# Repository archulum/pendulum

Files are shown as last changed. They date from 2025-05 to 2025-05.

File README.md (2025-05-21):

# The Electronic Pendulum by Arttu Lahti for Tampere University
This is the repository used to share important files and information on the Electronic pendulum BSc project. You can find the demo pendulum's 3D models, wiring diagram and parts list (with links) here. I also uploaded the Arduino scripts I used for my normal oscillation demos (both continuous and damped). The thesis itself is also here as a PDF file.

You're free to use and modify these files however you want, according to the MIT license (found in LICENSE.md).

For more information, check out the thesis.

Enjoy!

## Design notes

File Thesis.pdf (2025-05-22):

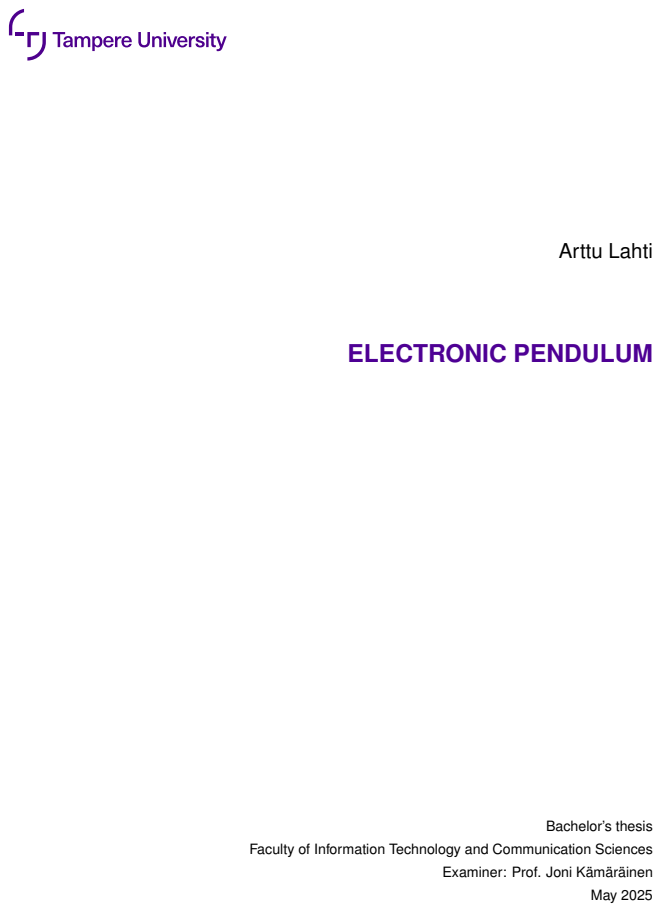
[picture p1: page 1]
Arttu Lahti; ELECTRONIC PENDULUM; Bachelor’s thesis; May 2025

Faculty of Information Technology and Communication Sciences

Examiner: Prof. Joni Kämäräinen

i

## ABSTRACT

Arttu Lahti: Electronic pendulum
Bachelor’s thesis
Tampere University
Bachelor’s Programme in Computing and Electrical Engineering May 2025

The pendulum is one of the simplest physical devices. Due to its simplicity, it is often represented on robotics, control and machine learning courses by simulations. However, there are upcoming courses at Tampere University, where the difference between simulations and the real world needs to highlighted, and a hands-on project is deemed beneficiary for the students. Given the predominant focus on simulations, there are very few, if any, simple electronic pendulums. This thesis explores existing research and projects already done on the subject, outlines the process of designing and building an electronic pendulum from scratch, and offers general instructions and an in-depth look into the thought process essential for building an electronic pendulum regardless of the available components.
Various article and thesis databases were consulted for the background information on past pendulum projects. One particular project stood out and was picked as the backbone of this project. The main electronic components of the pendulum are a DC motor, angular encoder, a motor driver and a single-board microcontroller. The components were picked carefully and it was made sure that they would work with each other. This process is detailed in the thesis, along with some things one must consider when doing the wiring work and designing the structure. Regarding the components and structure, some ideas and suggestions based on the difficulties experienced in building the demo pendulum are also provided along with the most critical warnings for the wiring. Some basic structural and functional testing was conducted and documented. The final demo product is a functional electronic pendulum that meets the testing criteria.

Keywords: robotics, pendulum, mechatronics, Arduino, electronics

The originality of this thesis has been checked using the Turnitin OriginalityCheck service.

ii

## TIIVISTELMÄ

Arttu Lahti: Elektroninen heiluri Kandidaatintyö
Tampereen yliopisto
Tieto- ja sähkötekniikan kandidaattiohjelma Toukokuu 2025

Heiluri on yksi yksinkertaisimmista fysikaalisista laitteista. Yksinkertaisuutensa vuoksi se saatetaan sivuuttaa robotiikan, säädön ja koneoppimisen kursseilla simulaatioiden tarjotessa lähes yhtä hyvän demonstraation. Tampereen yliopistolla on kuitenkin suunnitteilla kursseja, joissa oikean maailman ja simulaation ero on tarkoitus tuoda esille, ja mukaansatempaava fyysinen projekti olisi hyödyllinen opiskelijoille. Keskittyminen simulaatioihin on niin suurta, varsinkin tällä tasolla, että yksinkertaisia elektronisia heilureita on saatavilla erittäin heikosti, jos ollenkaan. Tässä työssä tutkitaan aiempia projekteja ja tutkimuksia, jotta saadaan käsitys saatavilla olevista heilureista ja työ käsittelee heilurin alusta asti suunnittelemisen ja rakentamisen vaiheet. Se myös tarjoaa yleisiä ohjeita ja syvemmän katsauksen siihen ajatusprosessiin, joka pitäisi olla perustana tällaista projektia toteuttavalla. Tarkoitus on, että tämän työn avulla henkilö pystyy suunnittelemaan ja rakentamaan elektronisen heilurin mistä vain saatavilla olevista osista.
Aluksi tutkittiin eri artikkeli- ja opinnäytetyötietokantoja taustatiedon keräämiseen aiemmista heiluriprojekteista. Yksi projekti valittiin tämän projektin perustaksi. Elektronisen heilurin tärkeimmät komponentit ovat tasavirtamoottori, kulmaenkooderi, moottoriohjain ja yhden levyn mikrokontrolleri. Komponentit valittiin huolella ja varmistettiin, että ne ovat toistensa kanssa yhteensopivia. Tämä prosessi on selitetty työssä johdotuksen ja rakenteen ohella. Työ tarjoaa myös yleisiä ohjeita ja ehdotuksia komponentteihin ja rakenteeseen liittyen perustuen demoheiluria rakennuksessa törmättyihin ongelmiin. Siinä on myös tämän kaltaiseen johdotukseen liittyviä varoituksia ja asioita, mitä ei kannata tehdä. Demoheilurille asetettiin ja tehtiin muutama perustesti liittyen rakenteeseen ja toimintaan. Valmis demoheiluri on toimiva elektroninen heiluri, joka täyttää testikriteerit.

Avainsanat: robotiikka, heiluri, mekatroniikka, Arduino, elektroniikka

Tämän julkaisun alkuperäisyys on tarkastettu Turnitin OriginalityCheck -ohjelmalla.

iii

## PREFACE

This was my first ever proper project involving electronics. When I saw the topics offered

to us, I decided to jump straight to the deep end, and here we are. I would like to extend my gratitude to Professor Joni Kämäräinen, my supervisor, for his support during every

part of the project and always being ready to listen and easy to communicate with. I would

also like to thank my friends and family for their support during the making of this project

and thesis.

Tampere, 22nd May 2025

Arttu Lahti

iv

The AI tools utilized in my thesis and their purposes are described below:

GPT-4o by OpenAI: GPT-4o was used to provide a massive help when figuring out the

electronic components and wiring of the pendulum to make sure everything is compatible

and safe. It was also a valuable and quick general assistant on different questions related

to the thesis.

ScopusAI by Elsevier: ScopusAI was used to find useful sources from Elsevier’s database

and to generate search words to use in Andor’s search function.

Apple Intelligence by Apple Inc.: Apple Intelligence provided fixes to the grammar and

structure of the entire text to ensure it is easy to understand and follows academic style.

I am aware that I am totally responsible for the entire content of the thesis, including

the parts generated by AI, and accept the responsibility for any violations of the ethical

standards of publications.

v

## CONTENTS

vi

## LIST OF SYMBOLS AND ABBREVIATIONS

b | viscous damping coefficient
cf | Coulomb friction coefficient
DC | Direct Current
E | total mechanical energy
g | gravity
I | moment of inertia
I/O | Input/Output
IDE | Integrated Development Environment
K | kinetic energy
L | pendulum arm length
m | pendulum mass
PC | Peak Current

PLA Polylactic Acid

RV | Rated Voltage
θ | angular position

θ

̇ angular velocity

θ

¨ | angular acceleration
TAU | Tampere University
τ | external torque from the motor
U | potential energy

## 1. INTRODUCTION

Pendulums are widely used in systems requiring control, mostly as benchmarking tools.

The most well-known example is the inverted pendulum, which is used in various exam-

ples, particularly in robotics and human locomotion analysis (Myers et al. 2020).

Most of the simple beginner-level control theory is taught with simulations. This may lead

students into thinking that physical real-world systems are as predictable as simulated environments, therefore, especially in robotics, learning with physical systems cannot

be substituted (Jara et al. 2011). A basic electronic pendulum provides students with

a connection to the real world that doubles as a physical, engaging, and dynamic system that can be used to experiment with control algorithms, reinforcement learning, and

signal processing. Due to the focus on simulations in entry-level studies, where simple

pendulums would be beneficial, simple electronic pendulums have been less explored

and documented. There were no readily available simple pendulums online that met the

criteria:

- reasonable tabletop size
- powered by a normal DC (Direct Current) motor
- able to follow programmed instructions to mimic realistic pendulum oscillation.

There are upcoming applications planned at TAU (Tampere University) for an electronic

pendulum on courses in robotics, signal processing, and machine learning. The objective of this thesis is not to provide a detailed tutorial on building an electronic pendulum, but

rather to offer insights into the thought process and the overall build and design process,

as well as the author’s considerations and reflections. Figure 1.1 depicts the 3D model of

the demo pendulum, whose design and building process was used to write this thesis.

The resources, such as models and scripts, used in building and testing the demo pendulum freely available at https://github.com/archulum/pendulum.

Chapter 2 provides an overview of control theory simulations, the fundamental principles

of a pendulum and various different designs for creating an electronic pendulum, and why

they do not fit the aim of this project. The aim of chapter 2 is not to go far into detail

on how a pendulum works, but highlight the phenomena that make a natural pendulum oscillate, aiming to provide further insight on how the motor could be controlled. Chapter

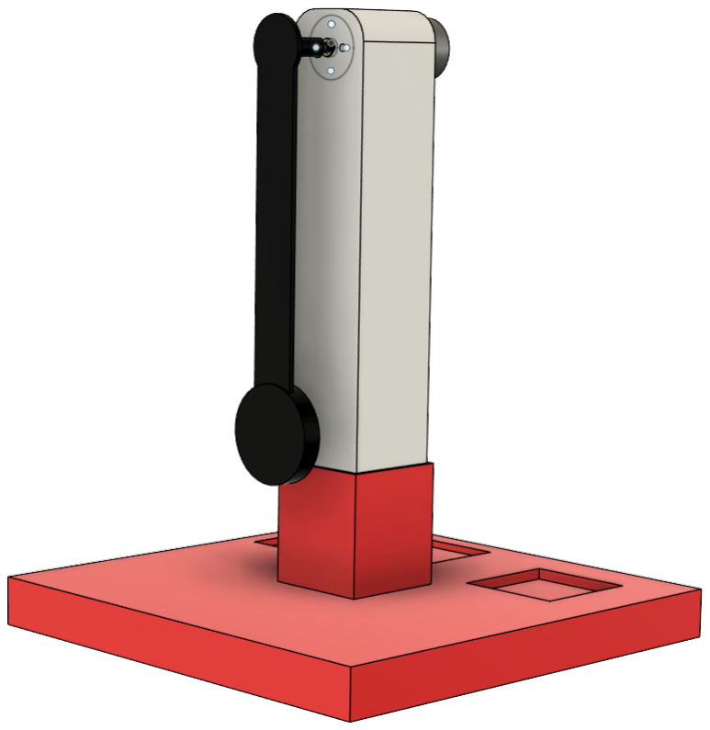
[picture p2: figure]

Figure 1.1. 3D model of the demo pendulum.

3 focuses on the parts, structure, design, assembly and testing of the pendulum. Chapter

4 presents the finished and assembled pendulum, as well as results of the tests and how well it handles all of its criteria. Chapter 5 opens a discussion on limitations and future

considerations, as well as gives the conclusion.

## 2. BACKGROUND

This chapter gives a brief overview on simulations, the fundamentals of a pendulum and

other motorised pendulums identified during the research phase.

### 2.1 Simulations

Simulations, by definition, are models of a real activity, created for training purposes or

to solve a problem (Cambridge University Press 2025). Generally, simulations are meth-

ods for analysing mechanisms using computers, as opposed to building the system or mechanism under investigation (Gardner 2001, p. 1). Simulations are especially good

and efficient in situations, where it might be financially or physically impossible to build

or setup a mechanism in real life. In general, simulations are easier to set up and they

provide results instantly, whereas physical research might have to be conducted for a long

time before any real and tangible results are received. A clear benefit of simulations is

also that the data gathered is always clean, which helps students better understand the

concept in question (De Jong et al. 2013). A study by Munoz Ubando et al. (2024) proposes that blurring the line between theory and practice, where the cycle of memorizing

concepts and applying them to real-life problems is shortened, proved to more beneficial

for students especially when the concept is complex and difficult.

When comparing simulations to physical tools, it is evident that using physical tools better prepares students to work more efficiently in real-life projects. They gain knowledge on

the things that can go wrong, like measurement errors, otherwise unusable data or equipment malfunction (De Jong et al. 2013). While using simulations as laboratory exercise

tools on courses has proven to be effective, allowing students to physically experiment

with equipment hands-on generates more motivation for the students (De Jong et al.

2013).

There are various methods for simulating pendulums. It can be done using MATLAB with Simulink, LabVIEW, Python or various other methods. MATLAB and Simulink, created

by The MathWorks, Inc., are widely used to aid computation and modelling of systems

(Bolton 2015, p. 605). MATLAB offers different toolboxes for performing specific tasks in different areas of study, such as control systems or signal processing (De Silva 2010,

p. 813). LabVIEW, by National Instruments, is a software development environment for

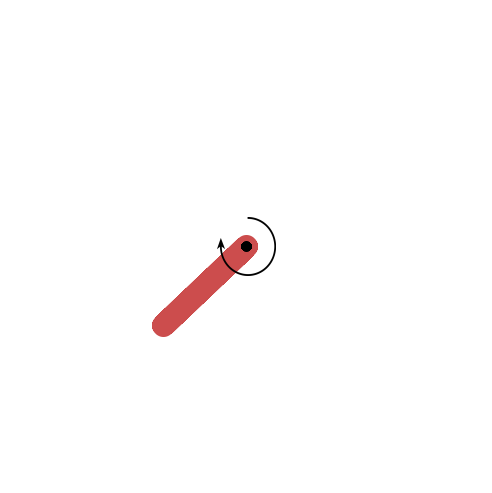
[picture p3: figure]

Figure 2.1. Screenshot of the gymnasium pendulum simulation. The arrow describes the direction and amplitude of the pendulum’s movement at the time of the screenshot.

data acquisition and instrument and motion control. It enables the user to create programs graphically similar to creating a flowchart (De Silva 2010, p. 829). Individual LabVIEW

programs mimic actual scientific instruments (Bolton 2015, p. 152), which makes it eas-

ier to understand especially to beginners. Additionally, the gymnasium library for Python, originally developed by OpenAI, includes a simulation of a pendulum (Towers et al. 2024),

which can be initiated in a Python program with just a few lines of code (Farama Founda-

tion 2025). Figure 2.1 depicts the pendulum from gymnasium.

### 2.2 Fundamental principle of a pendulum

A pendulum is a fundamental, simple mechanical system comprising a weight (bob) connected to a fixed point by an arm (rod or string) of length L. When the weight is displaced

from its equilibrium position and released, it moves periodically around the equilibrium

position. This repeating motion is called oscillation, occurring along a segment of a circle of radius L. The amplitude of the oscillation is influenced by gravity and L (Young 2016,

p. 474). In the context of a motor driven pendulum, an equation of motion is defined

(Wiebe et al. 2022)
Iθ¨ + bθ̇ + cf sign(θ
̇) + mgL sin(θ) = τ, | (2.1)

where Iθ¨ represents the rotational inertia as per Newton’s 2nd Law for Rotation, i.e. the

pendulum’s resistance to changes in its motion. bθ̇
represents viscous damping, where
the resistance force increases with the speed of the pendulum. cf sign(θ | ̇) accounts for

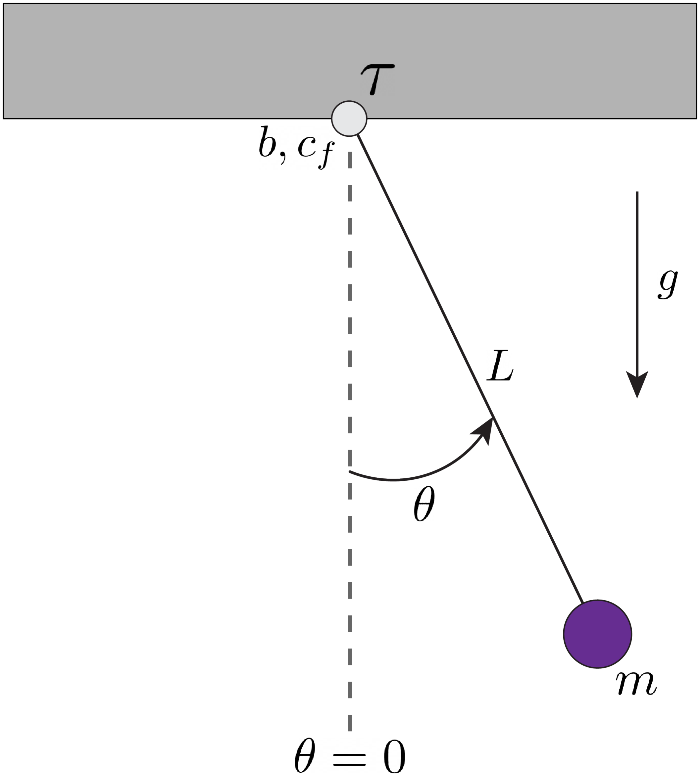
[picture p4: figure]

Figure 2.2. Drawing of a pendulum’s physical attributes according to the equation of motion in Equation 2.1. Reproduced and modified from (Wiebe et al. 2022).

dry friction, with sign(θ

̇) determining the direction of the friction force using the signum

function, which returns the sign of a value submitted to it (Venetis 2024). mgL sin(θ)

models the effect of gravity on the pendulum. τ denotes the torque applied by the motor.

The relations between the different terms are depicted in Figure 2.2.

When a pendulum bob is lifted from the equilibrium position, it gains potential energy.

When released, the bob goes back down to the equilibrium position and the potential energy is converted into kinetic energy. If it is not stopped at the equilibrium position,

it goes up to the opposite side and the kinetic energy converts back to potential energy

as the angular velocity decreases and the bob reaches its maximum amplitude (Baker

2006).

The equations for the potential (U), kinetic (K) and total mechanical (E) energies of the

pendulum are as follows (Wiebe et al. 2022; Young 2016)

U = −mgL cos(θ) | (2.2)

K =

1
2

mL²
θ

̇

2 | (2.3)
E = K + U. | (2.4)

In an ideal scenario, a pendulum would oscillate indefinitely without the need for a motor driving it. However, natural pendulums tend to dampen over time, per each oscillation, as shown on the left side of Equation 2.1. Potential, kinetic and mechanical energies in

Equations 2.2 – 2.4 diminish over time and eventually, when there is no energy left to transfer, the pendulum stops. As displayed in Equation 2.1, the torque τ the motor peri-

odically applies is there to add energy back into the system, preventing it from stopping

naturally.

### 2.3 Related works

Pendulums are one of the classic problems in control theory (Farama Foundation 2025),

which means there are many various ways to construct one for education or research

purposes. They are fundamentally the same in that they are powered by an electronic

actuator and are controlled by a microcontroller, usually an Arduino or a similar device. The largest difference between these versions is their method of generating the oscillation

motion.

The aeropendulum differs from the others in that the bob is also the provider of the

oscillation force. It has been done previously with a propeller connected to a brushless DC motor at the end of the arm (Neto et al. 2023; Vargová et al. 2023). Due to this, the

arm and bob must be as light as possible and to also achieve rigidity, are made of carbon fibre (Vargová et al. 2023).

The linear pendulum is easily the most common pendulum setup, and it is used in with-

out a doubt the most popular control problem and illustration: the pendulum on a cart (Choukchou-Braham 2014, p. 28). It can be done literally with a cart or a linear actuator

run with a belt. However, this results in the system usually being quite large, or at least requiring space to move around, and therefore is not feasible as a base for this project.

The vibration pendulum creates oscillation by vibrating the other end of the arm either

horizontally, vertically or both. They are rare especially in single-arm applications since it is very difficult to make it oscillate normally, and they are mostly used with two arms in

demonstrating chaotic properties since a double-arm vibration pendulum is the simplest way to demonstrate it (Gitterman 2008, pp. 53–60, 80–84).

The magnetic pendulum differs from the others in that it is the only one that fully allows

for completely natural pendulum movement since the arm is not attached to the source of

oscillation. It is driven by a coil magnet excited by a voltage source, usually located at the apex of the bob’s trajectory (Nyiembui et al. 2024). This setup has its good sides, but the

negatives outweigh the positives. It is not possible to stop a magnetic pendulum at any

location, nor is it possible to accelerate or decelerate it at will since it must always pass

by the apex point’s coil to adjust the movement.

A torque-driven inertia wheel pendulum, like the aeropendulum, is another pendulum that is actuated by the bob itself. It is a mechanism that consists of a symmetric disc

(a wheel), which is attached to the distal tip of the arm and is connected to an actuator capable of spinning parallel to the axis of rotation of the pendulum arm (Sandoval et al.

2021).

The simple pendulum, by Wiebe et al. (2022), with a rigid arm directly connected to the actuator, is the one this project will focus on, scaled down and reduced in cost.

## 3. METHODS

### 3.1 Parts and structure

This section provides an overview and details on picking the electrical components and the structural design. It also provides insight on what different things need to be consid-

ered to make the project safe for the user and equipment.

### 3.1.1 Electrical components

The electrical components as per the project’s backbone, Wiebe et al. (2022), suggests are an angular encoder, DC motor, motor driver, power supply and a single-board micro-

controller. Some basic wiring is necessary to connect everything together. The table of

electrical components for the demo pendulum is presented in Table 3.1.

Selecting the components for the project is a step that always requires careful attention.

Different electrical components have varying specifications regarding their rated and op-

erational voltages and currents. Every component connected to each other must not

exceed each other’s requirements, because doing so will result in unexpected behaviour or even component failure. If unsure or if the project is complex, one should make a table

to make sure all the components and their requirements and abilities work together. The full parts list of the demo pendulum is available on the GitHub page.

Table 3.2 should serve as the starting point, when considering the wide array of electri-

Table 3.1. Electrical components of the demo pendulum.

Item | Price (Quantity)
DC motor with encoder (6 – 24 V, 0.25 A) | 36.08 C (1)
L298N motor driver | 8.17 C (1)
Switching DC power supply (12 V, 1.6 A) | 20.40 C (1)
Arduino Uno R3 | 26.40 C (1)
1.5 mm² diameter wire | – (2 m)
Different jumper wires | –
Total | 91.05C

Table 3.2. Input and output specifications of each component of the demo pendulum.

Component | Input | Output | Notes
DC motor with encoder | RV: 12 V, PC: 250 mA | N/A | Output is sensor output, which is low enough for the Arduino and jumper wires.
L298N motor driver | RV: 7 – 30 V, PC: 2 A (1 A/channel) | N/A | The motor driver also has pins for wires com- ing from the Arduino. These are always rated for jumper wires.
DC power supply | Mains power | 12 V, 1.6 A | –
Arduino Uno R3 | 6 – 20 V* | Depends on pin: either 20 mA or 50 mA (Arduino Doc- umentation 2025). | *The Arduino can also be powered with USB power, especially when the motor driver han- dles the motor’s power needs.

cal components to select from. In simple terms, voltage represents the "pressure" that

pushes current through a circuit, while the used current is determined by the load of the component. Consequently, the voltage must not exceed the RV (Rated Voltage) and the

PC (Peak Current) drawn by the ultimate component must be lower than the main power

supply current.

Using Table 3.2, the demo pendulum was designed in such a way that everything works well with each other. The selected DC power supply provides 12 V at 1.6 A, which means

it has lower current capabilities than the PC of the motor driver. The motor draws a PC

of 250 mA, so the selected power supply is more than enough in the case of the demo

pendulum.

### 3.1.2 Structural components

The structural components of a tabletop electronic pendulum, as mentioned earlier, include the base, mast, arm and bob. All of these have various ways of implementing. One

approach is to make the pendulum using random pieces of wood or leftover metals. The

demo pendulum, however, aims for a 3D printed approach to maintain cleanliness and so

that students would not have to do 3D designing as part of the project. 3D printing is also

easy and quick, and revisions to the design can be done with ease. It also provides the simplest way of creating a structure that is reasonably straightforward to assemble and

disassemble. Figure 3.1 illustrates the 3D printed parts used in the demo pendulum. The 3D models used for the demo pendulum were created using Fusion 360 by Autodesk, Inc.

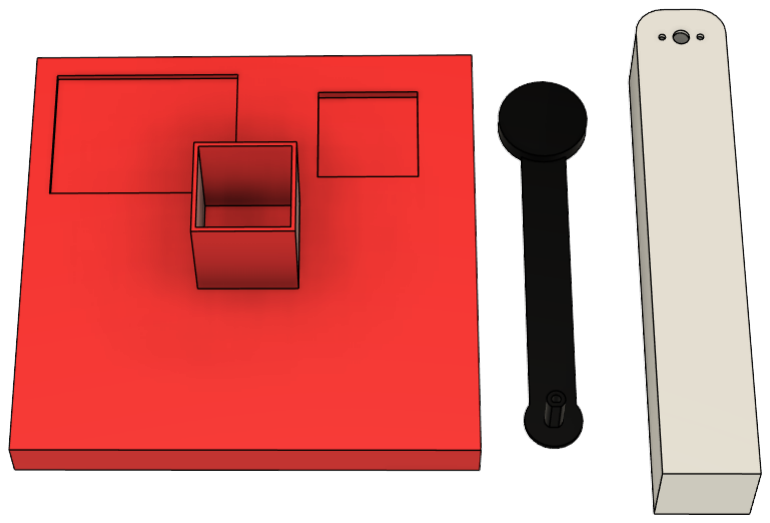
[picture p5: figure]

Figure 3.1. The 3D models of the demo pendulum’s structural components.

and are available to download on the GitHub page.

### 3.2 Assembly

This section will detail the wiring process and give some attention to important details that

must be noted when doing the wiring.

### 3.2.1 Wiring

The wiring for the demo pendulum is done as presented in Figure 3.2. The power supply is connected to a 2.1 mm adapter with 1.5 mm² wires leading to the L298N motor driver.

The thick wire is used for the connection to power the motor, as it is safer for higher

voltage and current wires to be thicker, especially when the pendulum might be swinging for longer durations of time, resulting in continuous loads on the wires. All other wires are jumper wires (0.2 mm² with DuPont style connectors), since they are able to handle the

voltage and current requirements of every other function of the pendulum.

The author of this thesis does not provide any safety warranties on the wiring. When

assembling the pendulum, several safety related issues should be kept in mind.

1. Under no circumstances should one work with mains power. Always use a certified

power supply to plug into the mains.

2. When working on the electronics and handling wires, the power supply should always be disconnected from the outlet.
3. The Arduino pins can only handle 20 mA or 50 mA currents. Motors should never be powered directly from the Arduino pins. Use a suitable motor driver.

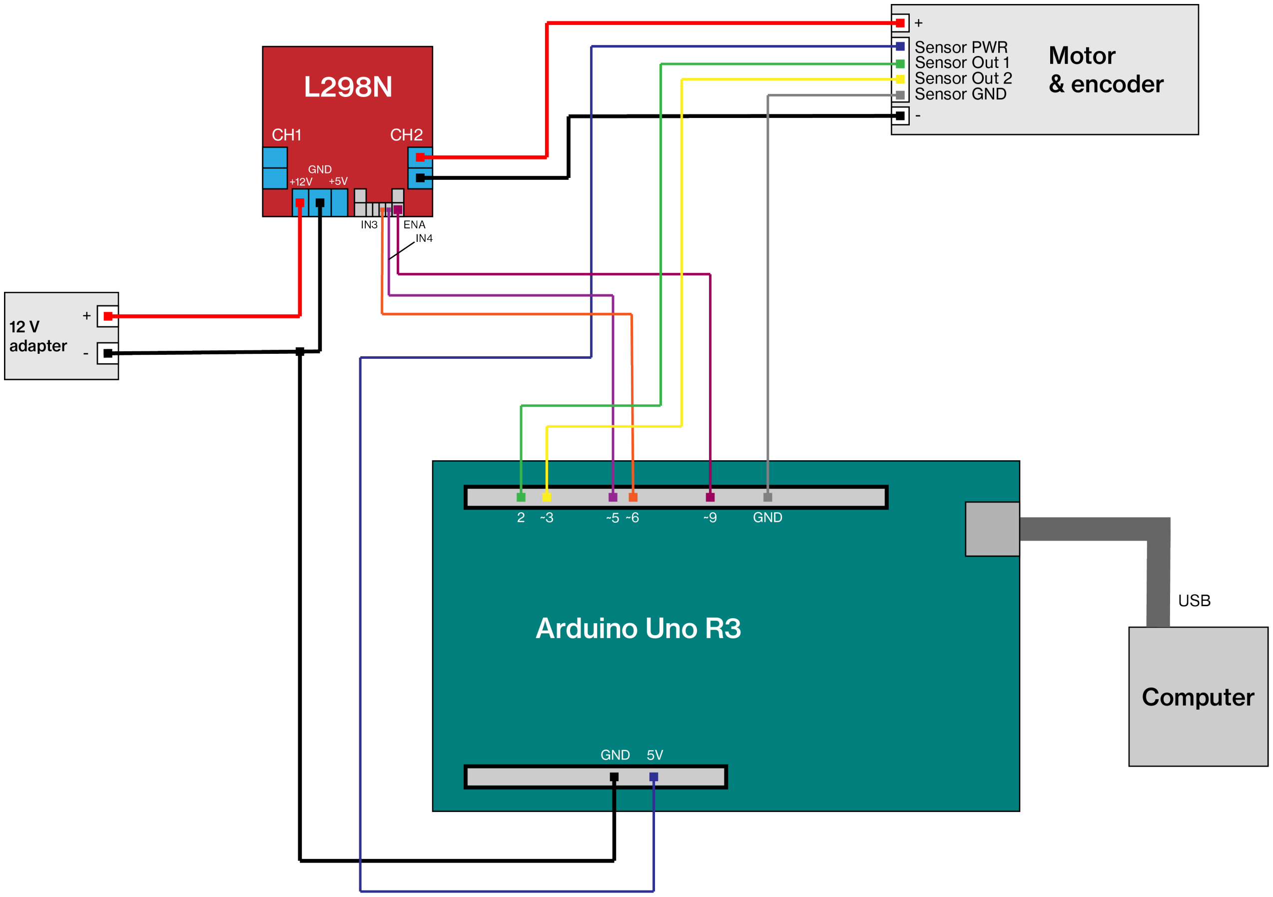
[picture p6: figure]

Figure 3.2. The wiring diagram of the demo pendulum.

### 3.2.2 Structure

The 3D printed base of the pendulum is of 200 × 200 × 20 mm in size. It includes

small cutouts to accommodate the Arduino Uno R3 and the L298N motor driver, so they do not freely roam about the table. A mast-shaped protrusion is also present on the

baseplate, providing support for the mast without compromising its overall height, while

also minimizing the need for extra screws. The mast is 230 mm tall and at the top it has a

housing for the motor with a 7 mm central hole for the axle and two 3 mm holes for screws

to secure the motor in place. The arm is 150 mm long. The components described above

are shown in Figure 3.1.

### 3.3 Oscillation with Arduino

The Arduino is an open-source electronics platform by Arduino ®, which focuses on ease-

of-use and breaking the barrier between the electronics design and rest of the world (Ar-

duino 2025). Arduino provides both hardware and software in the form of microcontroller

development boards and an IDE (Integrated Development Environment) that allows users to program the boards in Arduino Programming Language, a slightly altered version of C++ (Wikipedia contributors 2025). Arduino boards are used widely in education, proto-

typing, professional and hobbyist projects due to their strong community support, afford-

ability, and flexibility (Arduino 2025). For this project, the Arduino was chosen because of

its beginner-friendly nature.

The specific microcontroller used in the demo pendulum is the Arduino Uno R3. It offers sufficient digital and analog I/O (Input/Output) pins to interface with the angular encoder

and the L298N motor driver. It also provides a stable USB link with the host computer

for monitoring and debugging purposes, and for uploading the scripts. In this project, the

Arduino acts as the main controller for the pendulum system. It reads angular position

data from the motor encoder and sends control signals to the L298N motor driver, which

adjusts the motor’s torque accordingly. Depending on the control algorithm, the Arduino is capable of maintaining the pendulum in a passive swing state or be programmed to

stabilize it in an inverted position with a motor capable of handling it. The Arduino was

programmed using the Arduino IDE, which is available to download for free on the official

Arduino website. Basic motor control and data acquisition routines were implemented with serial communication used for debugging and to visualize data on the host computer

during testing.

### 3.4 Testing criteria

The testing of this project revolves around analysing the structural and functional capabil-

ities of the pendulum. It must be

- able to oscillate using the motor
- stay intact and upright, preferably on its own but if needed, different fastening meth-

ods shall be explored

- relatively easy to assemble and disassemble.

The functional capabilities can be assessed without the structural components, since it

only means the wiring is done correctly and every component in the circuit works as

intended. The structural integrity must wait until the physical components are created or otherwise procured. The ease of assembly, if using the provided 3D structure, should be

guaranteed.

## 4. RESULTS

### 4.1 Assembled pendulum

The 3D printed structural components of the pendulum fit together very tightly, as was

intended. The mast needed to be inserted into the holder with some force, but eventually

it was a good fit and the tightness ensures that the mast does not shake with the mo-

tor’s movements and high torque. Figure 4.1 depicts the fully assembled and connected

pendulum.

The pendulum was printed using PLA (polylactic acid), which is a strong and eco-friendly

bioplastic and a very popular filament for 3D printing. The base and arm were printed

with 15% infill and the mast with 5% infill, keeping the centre of gravity as low as possible.

PLA is known for its strength, making it suitable for indoor use. It is, however, brittle,

which calls for attention when inserting the mast into the holder as well as screwing in the

motor. If these are done with care, the material will endure the stress by the pendulum

itself easily.

### 4.2 Testing

If the project is replicated using the provided 3D models, the ease of assembly has already

been confirmed in previous chapters, and it was taken into account in every step of the

design process.

The motor was attached to the housing of the mast using screws, and the pendulum

arm was connected to its axle. An Arduino script mimicking normal pendulum oscillation was acquired using OpenAI GPT-4o and it was edited to fit this purpose, and also to not

have abrupt torque changes. With this script, the pendulum oscillates as expected, the motor goes from forward to reverse and follows the instructions sent over by the Arduino.

The encoder values also work correctly, which was confirmed using serial print-ins in

the Arduino IDE and supported by the fact that the pendulum always keeps the same

trajectory and does not, for example, rotate the "equilibrium" position (i.e. the apex point

of the trajectory) around. When oscillating, the pendulum stays intact, upright and it is

noticeably stable, removing the need for any fastening to the platform it stands on. Two

scripts, one for normal, continuous oscillation and one for normal, damped oscillation, are

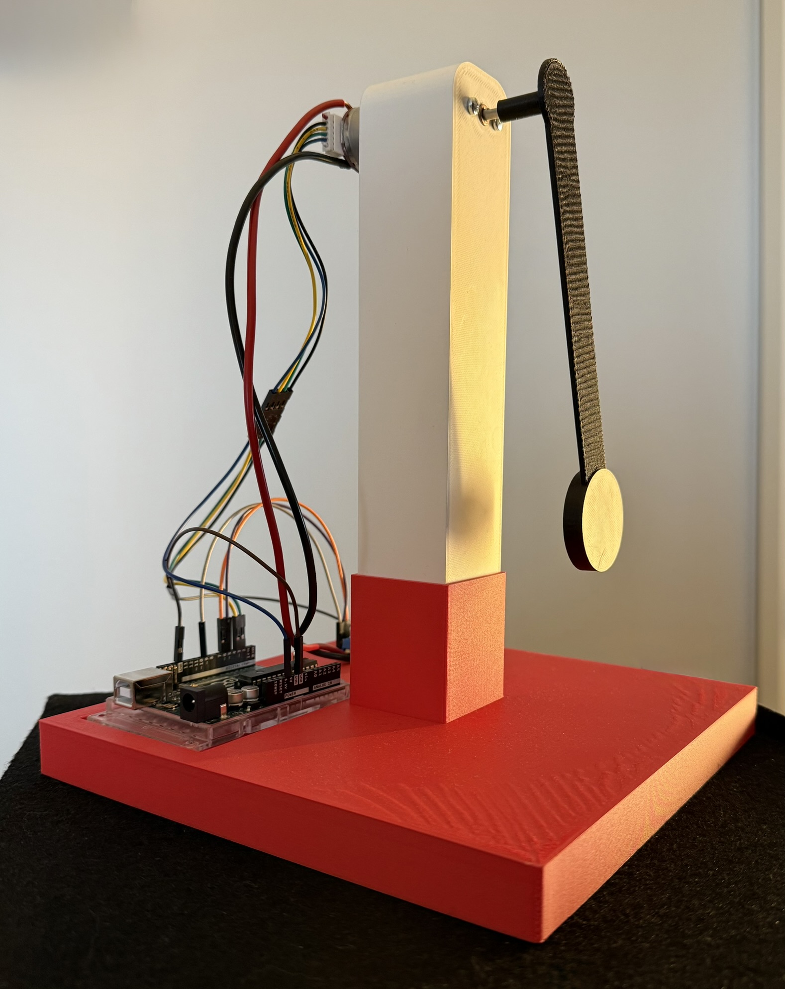
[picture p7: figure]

Figure 4.1. Finished and fully assembled demo pendulum.

available on the GitHub page.

## 5. DISCUSSION AND CONCLUSION

The finished pendulum meets the main criteria that were set in the introduction. However,

there are several of limitations and future considerations to address. Firstly, the motor

used in the demo pendulum was too stiff. This problem appears if one wants to use the

pendulum in a free-swinging state. This is quite difficult to overcome without sacrificing

other requirements. It would need a motor with a lower ratio gearbox or no gearbox at all, both of which would compromise the accuracy of the movements the motor is able to

make but also would most likely increase costs. The motor used in the project by Wiebe et al. (2022) is priced at over 500C, which is impractical for this kind of project.

Additionally, a motor with a higher maximum rotation speed than the motor used in the demo is recommended. The demo’s motor had a no-load speed of 128 rpm, which intro-

duced uncertainty during the design process, and the arm and bob of the pendulum had

to be made into a pseudo weight. In the demo, the arm and bob were a single 3D printed

object, which weighed only about 13 g. This ensured that the motor would handle it with no issues, as the schedule of the project did not allow for a redesign with a new motor,

motor driver and structure. Depending on the motor available, a real weight could be used, which would also open opportunities for writing scripts for more complex systems,

such as an inverted pendulum.

## REFERENCES

Arduino (2025). About Arduino | Arduino. URL: https://www.arduino.cc/en/about

(visited on 04/05/2025).
Arduino Documentation (2025). UNO R3 | Arduino Documentation. URL: https://docs.

arduino.cc/hardware/uno-rev3/ (https://docs.arduino.cc/hardware/uno-rev3/) (visited on 04/05/2025).

Baker, G. L. (2006). The pendulum : a case study in physics. eng. Ed. by J. A. Blackburn.

1st ed. Oxford scholarship online. Oxford: Oxford University Press. ISBN: 1-383-02974-
1. DOI: 10.1093/oso/9780198567547.001.0001. (https://doi.org/10.1093/oso/9780198567547.001.0001)

Bolton, W. (2015). Mechatronics : electronic control systems in mechanical and electrical

engineering. eng. Harlow: Pearson. ISBN: 978-1-292-07668-3.
Cambridge University Press (2025). SIMULATION | English meaning - Cambridge Dic-
tionary. URL: https : / / dictionary . cambridge . org / dictionary / english /

simulation (https://dictionary.cambridge.org/dictionary/english/simulation) (visited on 03/17/2025).
Choukchou-Braham, A. (2014). Analysis and control of underactuated mechanical sys-

tems. eng. Ed. by B. Cherki, M. Djemaï and K. Busawon. 1st ed. 2014. Gale eBooks. Cham, Switzerland: Springer. ISBN: 9783319026367. DOI: 10 . 1007 / 978 - 3 - 319 -

02636-7. (https://doi.org/10.1007/978-3-319-02636-7)
De Jong, T., Linn, M. and Zacharia, Z. (2013). Physical and virtual laboratories in science and engineering education. Science 340.6130, pp. 305–308. DOI: 10.1126/science.

1230579. (https://doi.org/10.1126/science.1230579)
De Silva, C. W. (2010). Mechatronics : a foundation course. eng. Boca Raton: CRC. ISBN:

978-1-4200-8211-1.
Farama Foundation (2025). Pendulum - Gymnasium Documentation. URL: https : / /

gymnasium.farama.org/environments/classic_control/pendulum/ (visited

on 03/17/2025).
Gardner, J. F. (2001). Simulations of machines using Matlab and Simulink. eng. Bookware

companion series. Pacific Grove: Brooks/Cole. ISBN: 0-534-95279-8.

Gitterman, M. (2008). The noisy pendulum. eng. 1st ed. New Jersey: World Scientific.

ISBN: 9789812833006.
Jara, C. A., Candelas, F. A., Puente, S. T. and Torres, F. (Dec. 2011). Hands-on experi-

ences of undergraduate students in Automatics and Robotics using a virtual and remote laboratory. Computers & Education 57.4, pp. 2451–2461. ISSN: 0360-1315. DOI: 10.1016/J.COMPEDU.2011.07.003. (https://doi.org/10.1016/J.COMPEDU.2011.07.003)

Munoz Ubando, L., Amigud, A. and Sirazitdinova, E. (2024). Computer simulation and

hands-on labs: A case study of teaching robotics and AI. International Journal of Mechanical Engineering Education. DOI: 10.1177/03064190241240416. (https://doi.org/10.1177/03064190241240416)

Myers, A. D., Tempelman, J. R., Petrushenko, D. and Khasawneh, F. A. (Oct. 2020). Low-

cost double pendulum for high-quality data collection with open-source video tracking and analysis. HardwareX 8, e00138. ISSN: 2468-0672. DOI: 10.1016/J.OHX.2020.

E00138. (https://doi.org/10.1016/J.OHX.2020.E00138)
Neto, R. C., Trindade, F. L. A., Marques, B. R. A., Azevedo, G. M. S., Barbosa, E. J. and

Barbosa, E. A. O. (2023). An Aeropendulum-Based Didactic Platform for the Learning

of Control Engineering. eng. Journal of control, automation & electrical systems 34.3, pp. 566–577. ISSN: 2195-3880. DOI: 10.1007/s40313-022-00981-4. (https://doi.org/10.1007/s40313-022-00981-4)

Nyiembui, P. T., Zambo, A. M. N., Nana, B. and Woafo, P. (2024). Dynamical behavior of

a vertical magnetic pendulum driven by one coil magnet excited by a voltage source. eng. Nonlinear dynamics. ISSN: 0924-090X. DOI: 10.1007/s11071-024-10663-2. (https://doi.org/10.1007/s11071-024-10663-2)

Sandoval, J., Kelly, R. and Santibáñez, V. (2021). An Output Feedback Position/Speed

Regulator for a Torque—driven Inertia Wheel Pendulum. eng. International journal of

control, automation, and systems 19.10, pp. 3451–3463. ISSN: 1598-6446. DOI: 10. 1007/s12555-020-0744-7. (https://doi.org/10.1007/s12555-020-0744-7)

Towers, M., Kwiatkowski, A., Terry, J., Balis, J. U., De Cola, G., Deleu, T., Goulão, M.,

Kallinteris, A., Krimmel, M., KG, A., Perez-Vicente, R., Pierré, A., Schulhoff, S., Tai,

J. J., Tan, H. and Younis, O. G. (July 2024). Gymnasium: A Standard Interface for Reinforcement Learning Environments. URL: https://arxiv.org/abs/2407.17032v3.

Vargová, A., Boldocký, J., Gulan, M., Tibenský, P., Mikuláš, E. and Takács, G. (2023).

AeroShield: An Open-Source Propeller-Driven Pendulum Device for Control Engineer-

ing Education. eng. IFAC-PapersOnLine 56.2, pp. 9600–9605. ISSN: 2405-8963. DOI: 10.1016/j.ifacol.2023.10.264. (https://doi.org/10.1016/j.ifacol.2023.10.264)

Venetis, J. (Oct. 2024). An Explicit Form of Signum Function. Mathematics 12.20, p. 3246. ISSN: 2227-7390. DOI: 10.3390/MATH12203246. (https://doi.org/10.3390/MATH12203246) URL: https://www.mdpi.com/

2227-7390/12/20/3246. (https://www.mdpi.com/2227-7390/12/20/3246)

Wiebe, F., Babel, J., Kumar, S., Vyas, S., Harnack, D., Boukheddimi, M., Popescu, M. and

Kirchner, F. (2022). Torque-limited simple pendulum: A toolkit for getting familiar with control algorithms in underactuated robotics. Journal of Open Source Software 7.74,
p. 3884. DOI: 10.21105/joss.03884. (https://doi.org/10.21105/joss.03884) URL: https://doi.org/10.21105/joss.

03884. (https://doi.org/10.21105/joss.03884)
Wikipedia contributors (2025). Arduino — Wikipedia, The Free Encyclopedia. URL: https: //en.wikipedia.org/w/index.php?title=Arduino&oldid=1282405415 (visited

on 04/27/2025).

Young, H. D. (2016). University physics with modern physics. eng. Ed. by R. A. Freedman

and A. L. Ford. 14. global ed. Harlow: Pearson. ISBN: 978-1-292-10031-9.

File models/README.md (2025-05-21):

# Models folder
This folder contains the 3D models for the demo pendulum. Created using Autodesk Fusion 360.

The STL folder includes the models for the structure of the demo pendulum, ready for 3D printing if needed. The STP folder includes the 3D model files for editing, if you do not have the same parts at hand as the demo did.
Fusion 360 was used to create them, but .stp files can be edited with any 3D design software.

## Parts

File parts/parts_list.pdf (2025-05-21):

## Electronic pendulum parts list

Arduino Uno R3, 26.40€:
https://www.partco.fi/fi/arduino/arduino-classic/15335-arduino-uno.html L298N motor driver, 8.17€: https://www.partco.fi/fi/saehkoemekaniikka/moottorit/moottoriohjaimet/25 737-mot-mdl298n.html (https://www.partco.fi/fi/saehkoemekaniikka/moottorit/moottoriohjaimet/25737-mot-mdl298n.html)
DC motor w/ angular encoder, 36.08€: https://www.partco.fi/fi/saehkoemekaniikka/moottorit/dc-moottorit/21183-mot-ams60085m.html (https://www.partco.fi/fi/saehkoemekaniikka/moottorit/dc-moottorit/21183-mot-ams60085m.html)
DC power supply 12 V, 1.6 A, 20.40€: https://www.partco.fi/fi/teholaehteet/hakkurit/kiinteaet-dc-hakkurit/15908-cps-12v1600.html (https://www.partco.fi/fi/teholaehteet/hakkurit/kiinteaet-dc-hakkurit/15908-cps-12v1600.html)
DC adapter 2,1 mm, 3.40€:
https://www.partco.fi/fi/liittimet/virtaliittimet/dc-liittimet/10891-dcj21ruu.html (https://www.partco.fi/fi/liittimet/virtaliittimet/dc-liittimet/10891-dcj21ruu.html)
2x U-N jumper wires (DuPont connectors) 18 cm 10kpl, 2 x 8.00€: https://www.partco.fi/fi/protoilu/hyppylangat/17332-jmp-un15-sek.html USB 2.0 A-male–B-male, 3.90€: https://www.partco.fi/fi/tietokonetarvikkeet/vaeylaet/usb/usbkaapelit/10305-dk-usb-vj2-1m.html (https://www.partco.fi/fi/tietokonetarvikkeet/vaeylaet/usb/usb-kaapelit/10305-dk-usb-vj2-1m.html)

You will also need:
- 2x 1 m 1.5 mm² wire for power connections. Available online or at a local electronics store.

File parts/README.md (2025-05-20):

# Parts folder
This folder includes the parts list of the demo pendulum. Feel free to use it to order your own parts (or similar/better ones).

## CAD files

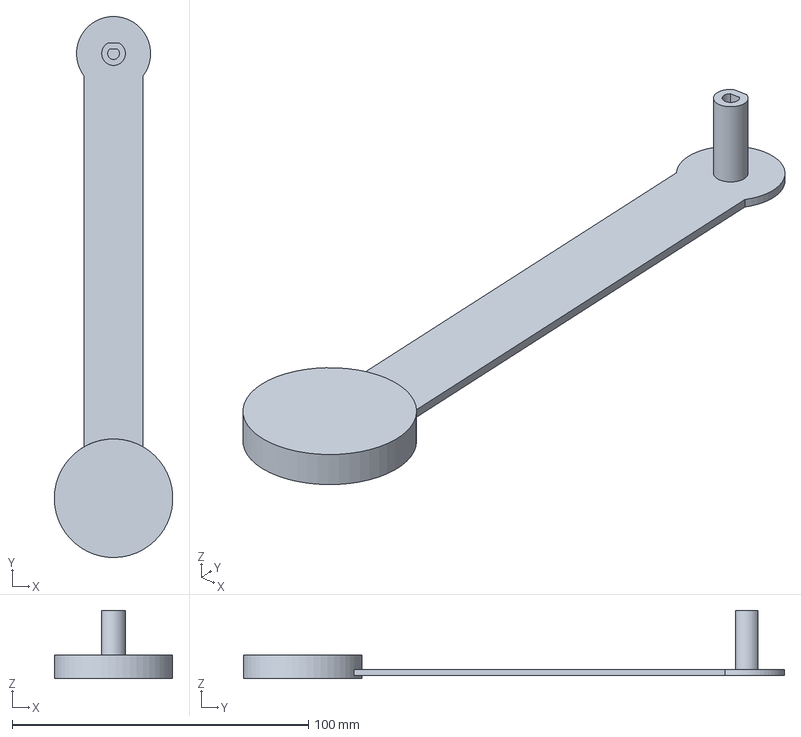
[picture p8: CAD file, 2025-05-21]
models/stp/Arm.step
40.0 x 182.5 x 23.0 mm

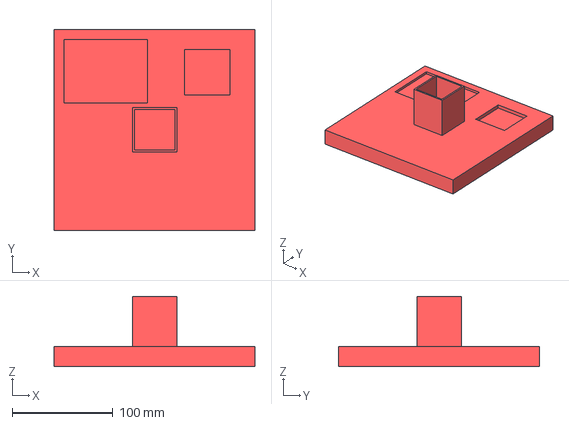
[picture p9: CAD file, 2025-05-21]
models/stp/Baseplate.step
200.0 x 200.0 x 70.0 mm

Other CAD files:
models/stl/Arm.stl
models/stl/Baseplate.stl

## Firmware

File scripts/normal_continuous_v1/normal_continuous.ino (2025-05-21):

#define IN1 5
#define IN2 6
#define ENA 9

#define ENCODER_A 2
#define ENCODER_B 3

volatile long encoderCount = 0;
int direction = 1;
int maxTicks = 255;
int baseSpeed = 90;
int currentSpeed = baseSpeed;
int damping = 1;

void setup() {
  // put your setup code here, to run once:
  pinMode(IN1, OUTPUT);
  pinMode(IN2, OUTPUT);
  pinMode(ENA, OUTPUT);

  pinMode(ENCODER_A, INPUT_PULLUP);
  pinMode(ENCODER_B, INPUT_PULLUP);

  attachInterrupt(digitalPinToInterrupt(ENCODER_A), readEncoder, CHANGE);
  attachInterrupt(digitalPinToInterrupt(ENCODER_B), readEncoder, CHANGE);

  Serial.begin(9600);

  encoderCount = 0;
  swingMotor(direction, currentSpeed);

}

// motor swing, changes the motor driver H-bridge connections around
void swingMotor(int dir, int speed) {
  if (dir > 0) {
    digitalWrite(IN1, HIGH);
    digitalWrite(IN2, LOW);
  } else {
    digitalWrite(IN1, LOW);
    digitalWrite(IN2, HIGH);
  }

  analogWrite(ENA, speed);
}

// encoder reading function, increases by one when signals match
void readEncoder() {
  bool A = digitalRead(ENCODER_A);
  bool B = digitalRead(ENCODER_B);

  if (A == B) {
    encoderCount++;
  }
}
void loop() {

  // print encoder count in the serial
  static long lastPrinted = 0;
  if (millis() - lastPrinted > 100) { // every 100ms
    Serial.println(encoderCount);
    lastPrinted = millis();
  }
  
  int distance = abs(encoderCount);
  int effectiveSpeed = currentSpeed;

  // slowing the swing down near the max amplitude to improve realism
  if (distance > maxTicks*0.7) {
    float scale = pow(1.0 - ((float)(distance - maxTicks * 0.7) / (maxTicks * 0.2)), 2);
    effectiveSpeed = max(currentSpeed * scale, 30);
  }

  swingMotor(direction, effectiveSpeed);

  //Change direction at the end of swing
  if (distance >= maxTicks) {
    direction *= -1;
    encoderCount = 0;
    
    delay(200);
  }
}

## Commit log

2025-05-21 Uploaded stl and stp files for the baseplate, mast and arm.
    [Arm.step, Arm.stl, Baseplate.step, Baseplate.stl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]
2025-05-21 Uploaded the wiring diagram.
